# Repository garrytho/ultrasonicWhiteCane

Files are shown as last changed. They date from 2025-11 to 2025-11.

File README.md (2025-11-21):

# Ultrasonic Distance-Sensing White Cane
<table>
  <tr>
    <td align="center">
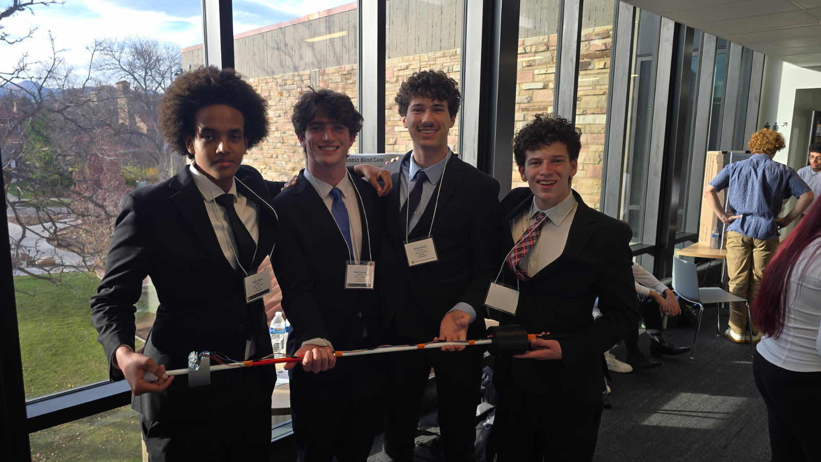
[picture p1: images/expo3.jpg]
      <br>
      <em>The fully assembled cane on expo day</em>
    </td>
    <td align="center">
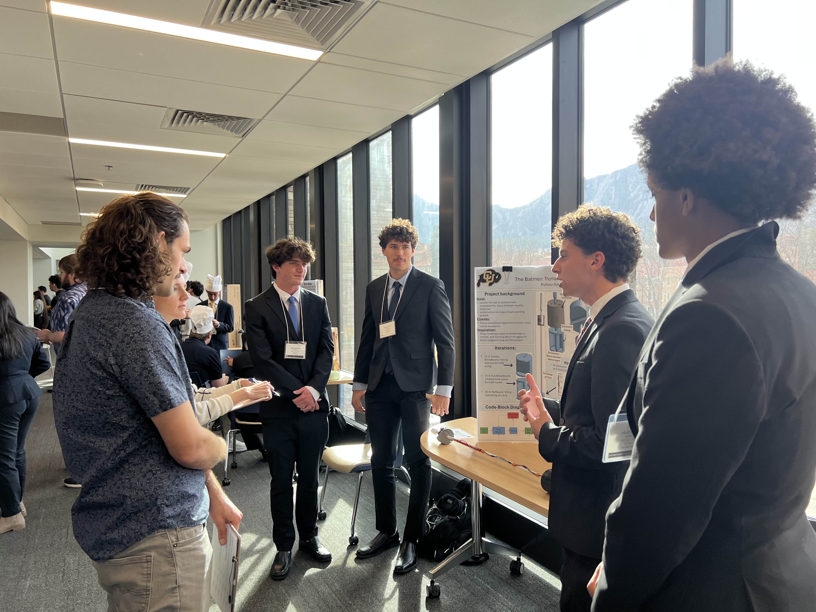
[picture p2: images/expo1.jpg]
      <br>
      <em>The team delivering the pitch</em>
    </td>
  </tr>
</table>

An Arduino-based cane for the visually impaired that uses a distance sensor and haptic feedback to give real time information about surroundings. 

## Update:
<table>
  <tr>
    <td align="center">
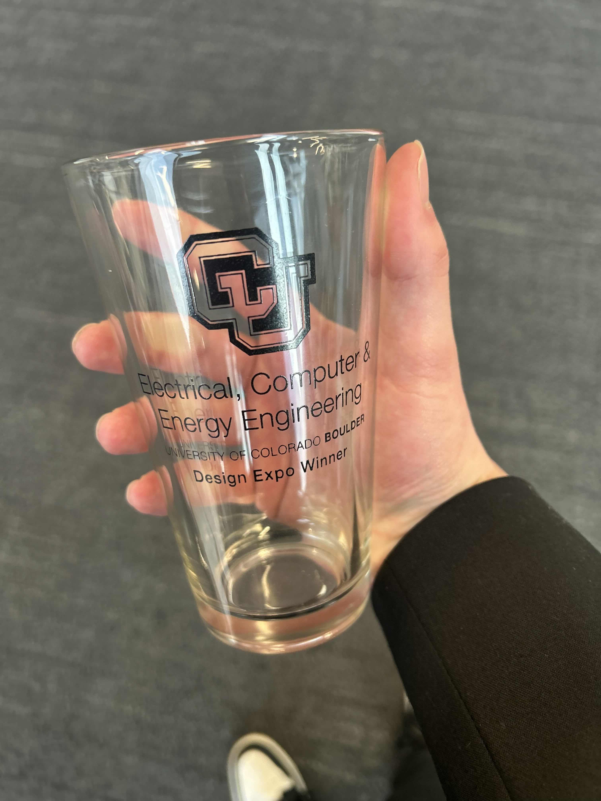
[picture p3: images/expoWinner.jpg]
      <br>
      <em>We are excited to announce that this project has won a freshman design award after judging at expo. 
</em>
  </tr>
</table>

## IMPORTANT:
This project is a work in progress. Iteration and modification may be necessary for reliable daily usage!

## Overview
Our project is a modified blind cane for the visually impaired that helps to reduce collisions while navigating. To accomplish this, we implemented an ultrasonic distance sensor along with a buzzer to alert the user when they are close to objects through vibration and sound. By using readily available components, 3D printed housing, and a pre-existing blind cane, we have created a widely accessible and affordable navigational aid. Our white cane is much cheaper to produce than commercially available alternatives, and is entirely open source for improvements and alterations. We hope that our resourceful design empowers more users with greater confidence and independence.

## Images and Demonstrations
<table>
  <tr>
    <td align="center">
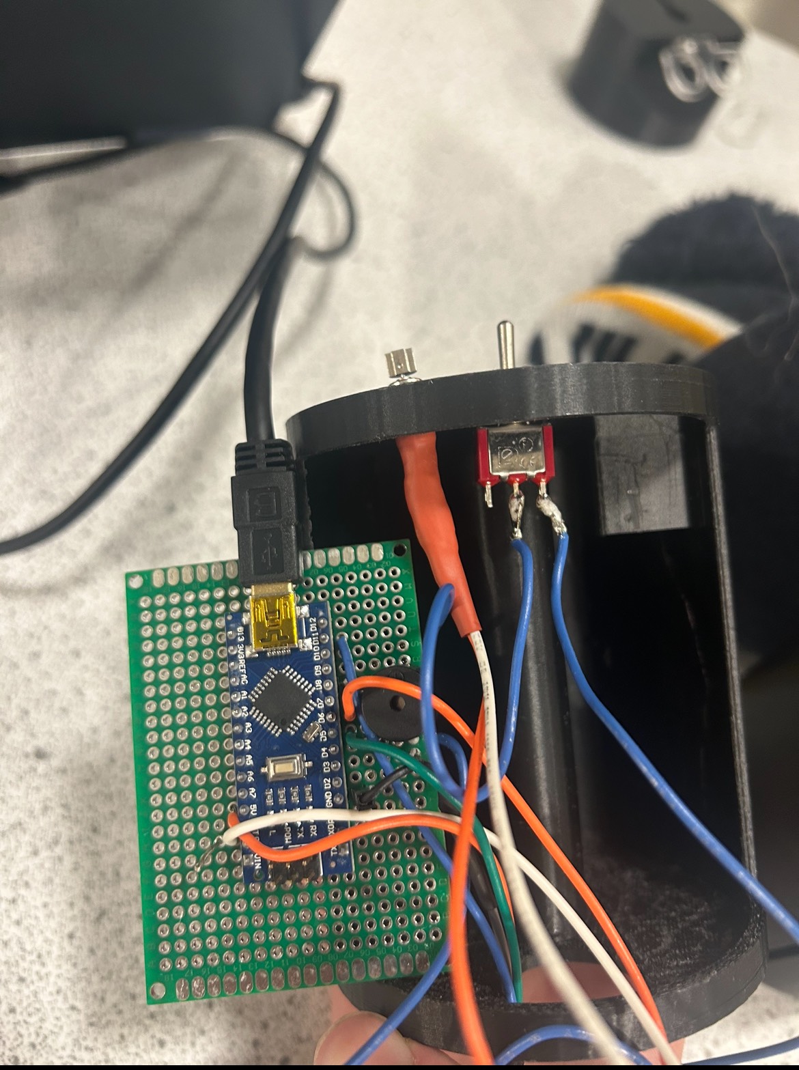
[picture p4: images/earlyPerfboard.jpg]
      <br>
      <em>Our first soldered perfboard being fitted into the case </em>
    </td>
    <td align="center">
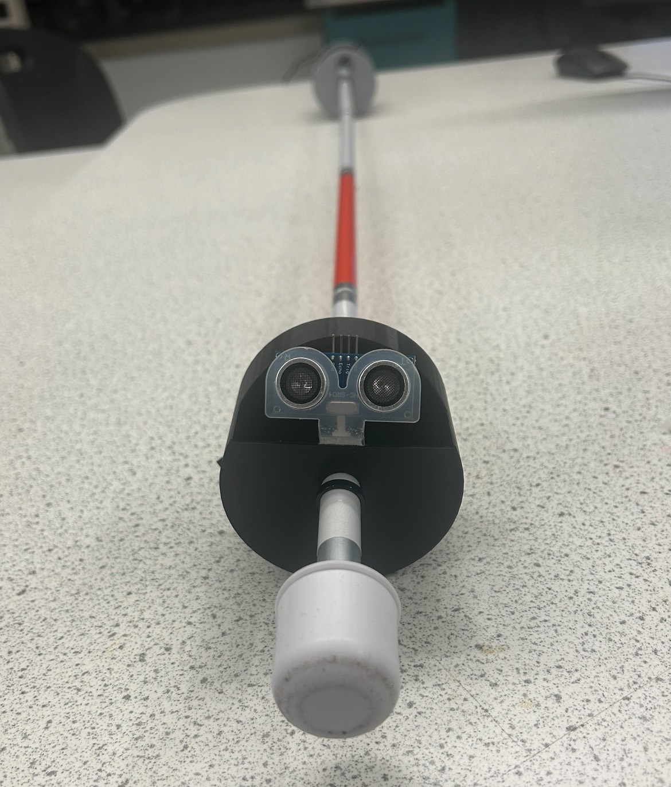
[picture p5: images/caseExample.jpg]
      <br>
      <em>The second iteration of the sensor mount </em>
    </td>
    <td align="center">
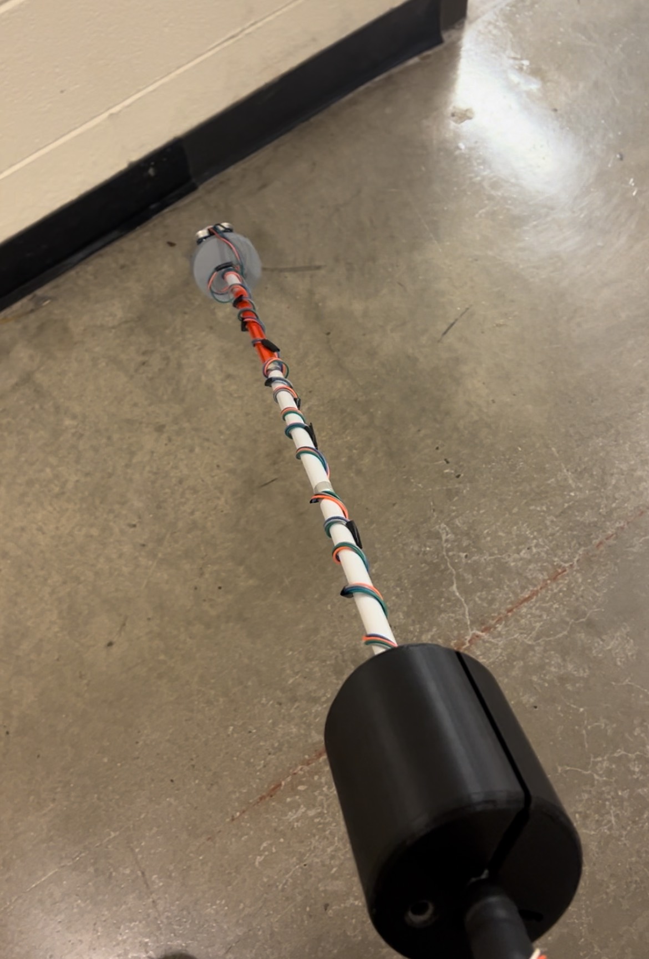
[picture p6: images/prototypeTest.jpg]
      <br>
      <em>A fully assembled initial prototype</em>
    </td>
  </tr>
</table>

### [Click here to watch the demo video](https://youtube.com/shorts/pAP-bUpbX8s?feature=share)

## Features
-Entirely open sourced
-Much cheaper to produce as compared to commercial alternatives
-Rechargable battery via USB-C for accessibility
-Weight distribution is optimal for daily navigation

## Cost of development vs. commercial alternatives

| Device | Price per Unit | Precision | Notes |
|--------|----------------|-----------|-------|
| [WeWalk Smart Cane 2](https://floridareading.com/products/wewalk-smart-cane-2-with-voice-assistant) | $1,050 | High | Extremely expensive, but has extensive features. |
| **This White Cane** | **~$51.69** | Mid | Highly affordable, and possible to build yourself. Open sourced for wider accessilibility and to encourage innovation in the assistive tech space. |

## Use Cases and Applications

# BILL OF MATERIALS

| # | Item               | Purpose           | Qty. | Cost/Unit Part | Cost |
|---|--------------------|------------------|------|----------------|------|
| 1 | HC-SR04            | Ultrasonic Sensor | 1    | $4             | $4   |
| 2 | Arduino Nano       | Microcontroller   | 1    | $5             | $5   |
| 3 | JYCL0610R2540      | Vibration Motor   | 3    | $2             | $6   |
| 4 | MakerFocus 3.7V 3000mAh Lipo | LiPo Batteries | 2 | $9 | $18 |
| 5 | MT3608             | Step Up           | 1    | $1             | $1   |
| 6 | TP4056             | Charge Protector  | 1    | $2             | $2   |
| 7 | Cane               | Cane              | 1    | $15            | $15  |
**Total:** $51

## Hardware Overview
<p align="center">
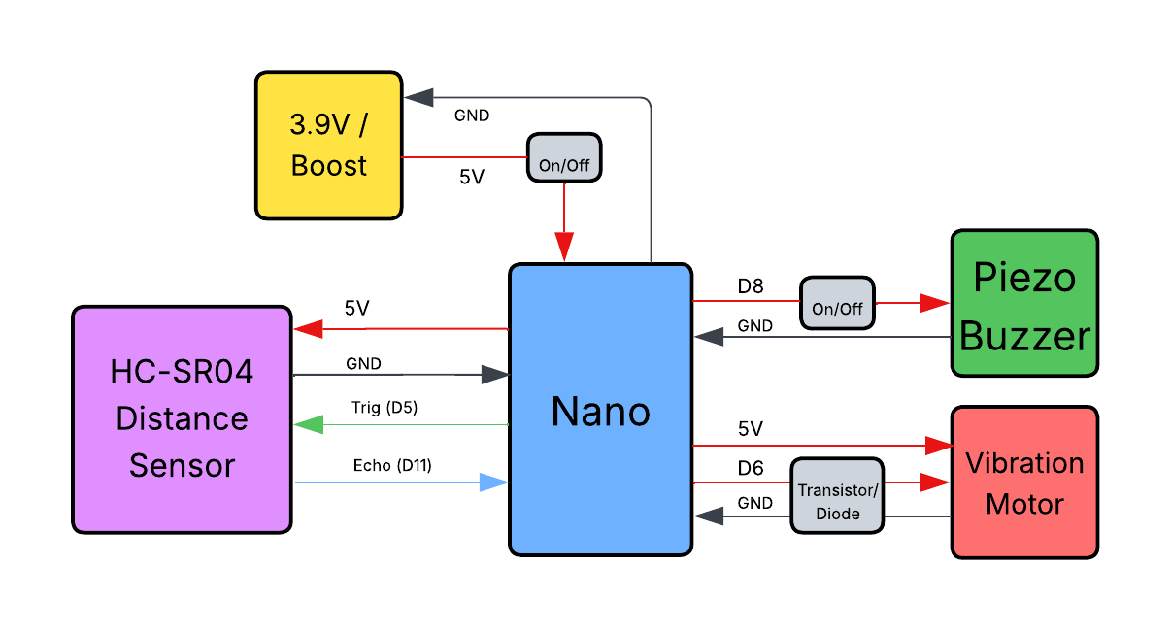
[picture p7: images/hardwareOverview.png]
  <br>
</p>

### Pin Assignments

**Power**:
- **+5v** - +5V from Boost Module
- **GND** - GND from Boost Module

**Distance Sensing**:
- **+5V** - VCC pin on the HC-SR04
- **GND** - GND pin on the HC-SR04
- **D5** - Trig pin on the HC-SR04
- **D11** - Echo pin on the HC-SR04

**Sound Cue**: 
- **D8** - VCC pin on the piezo buzzer
- **GND > Switch** - Toggles GND pin on the piezo buzzer (on/off)
  
**Haptic Cue**:
- **+5v** - VCC pin on vibration motor
- **D6** - Base pin on control transistor
- **GND > Transistor/Diode** - Emitter and collector lines for vibration motor control. 

### Setup Instructions
- Assemble the circuit as described above
- Connect the Arduino board to your computer via USB
- Open the provided .ino file in the Arduino IDE
- Select the appropriate port and board type (Nano)
- Upload the code to the Nano
- Disconnect from USB and power via LiPo

### Code Snippet
```cpp
//Take one distance reading (in cm)
long distance = pingDistance();

//Filter for valid readings
if (distance > 0 && distance < 120) {

  // Map distance to tone: closer = higher urgency
  int toneFreq = map(distance, 1, 120, 5000, 500);
  tone(8, toneFreq, 200);   // buzzer on pin 8

  // Vibration motor: full power at or below 60 cm
  if (distance <= 60) {
    analogWrite(vibPin, 255);   // ON
  } else {
    analogWrite(vibPin, 0);     // OFF
  }
}
```
For the full firmware, see [whiteCaneV6_Simplified_Clean.ino](whiteCaneV6_Simplified_Clean.ino)

### Hardware Limitations & Planned Improvements
| Issue                    | Description                                              | Planned Fix                                                                 |
|--------------------------|----------------------------------------------------------|------------------------------------------------------------------------------|
| Battery reliability      | 5V LIPO is vulnerable to weather interference.                  | Improve waterproofing and make the housing more robust|
| Sensor Accuracy      | The HC-SR04 alone can sometimes yield inconsistent results, especially with objects that scatter sound.                 | Integrate a second sensor (time of flight) and cross reference readings.|
| Housing       | Our current housing doesn't mechanically secure certain components in the circuitry box.                  | Add dedicated segments with mounting screws / threadded holes for securing components. |

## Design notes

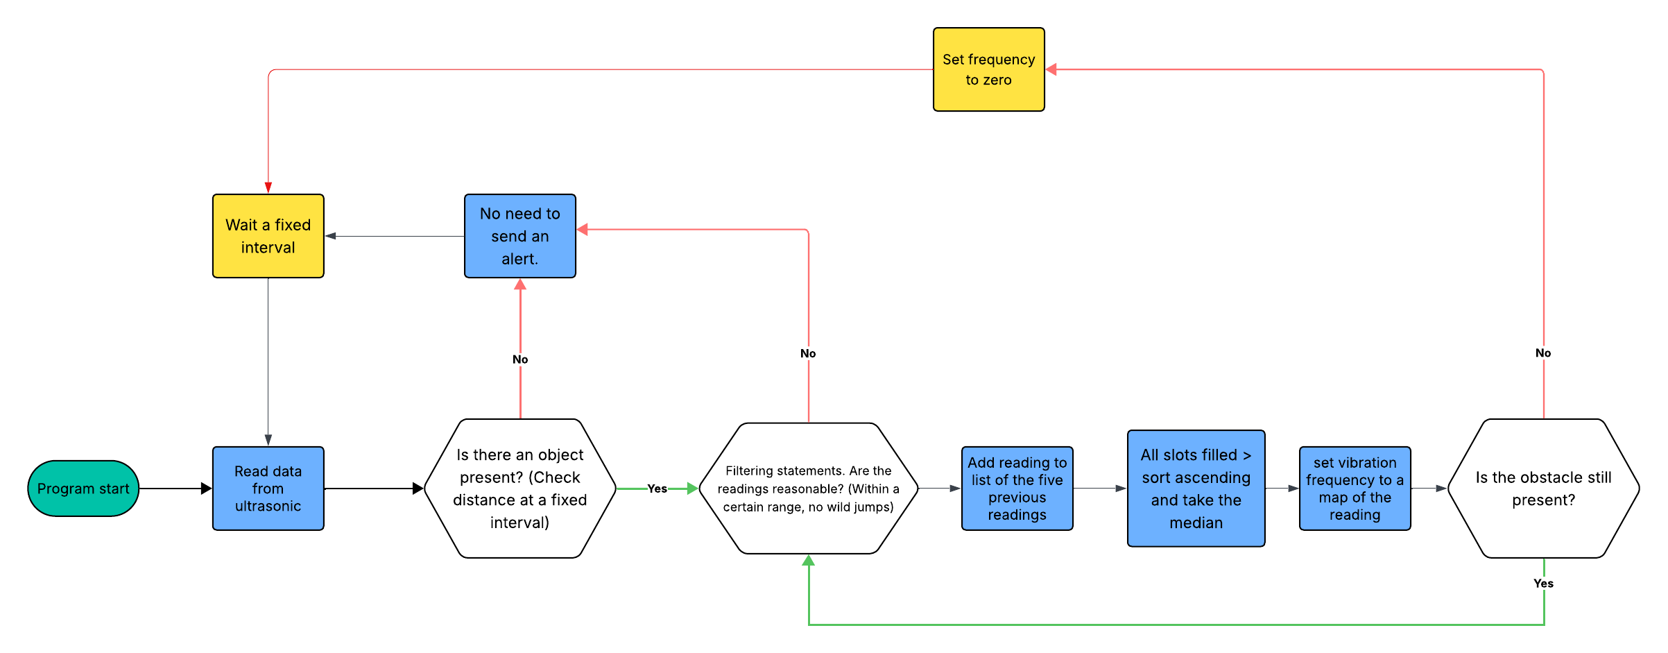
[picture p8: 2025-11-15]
images/codeOverview.png

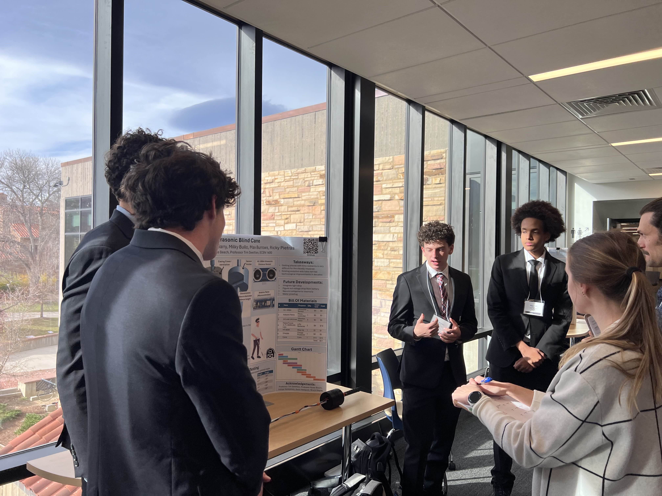
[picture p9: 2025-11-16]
images/expo2.jpg

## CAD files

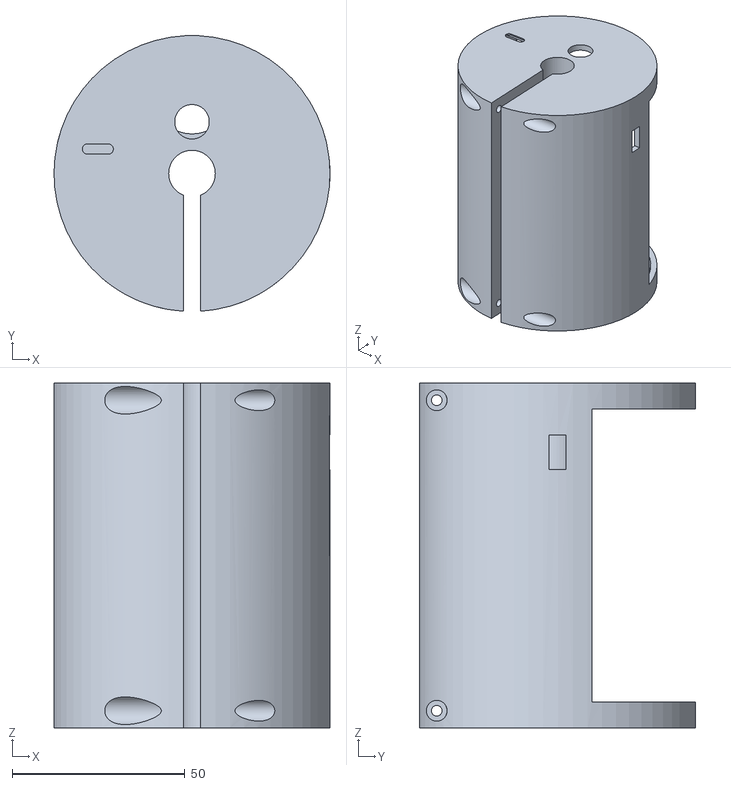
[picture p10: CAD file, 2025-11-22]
onShape/Main Housing V2.stl
80.0 x 79.9 x 100.0

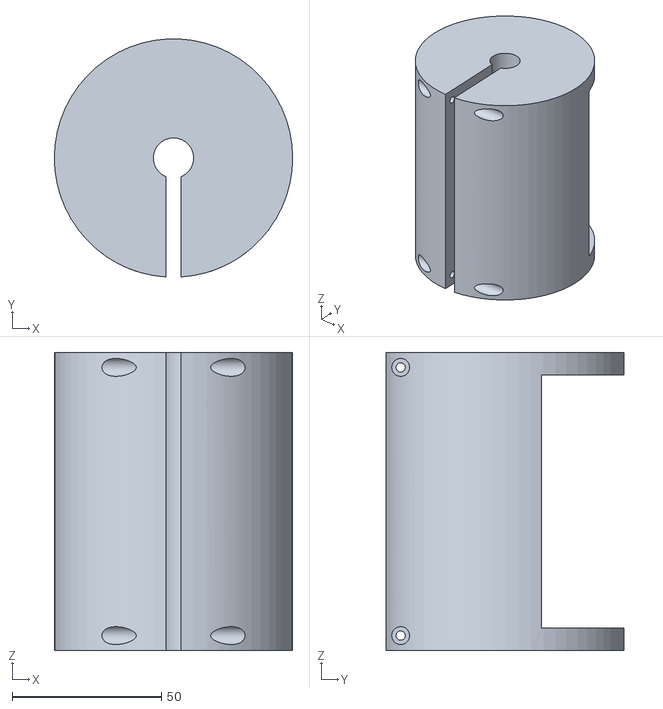
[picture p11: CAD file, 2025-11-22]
onShape/Main Housing V1.stl
80.0 x 79.9 x 100.0

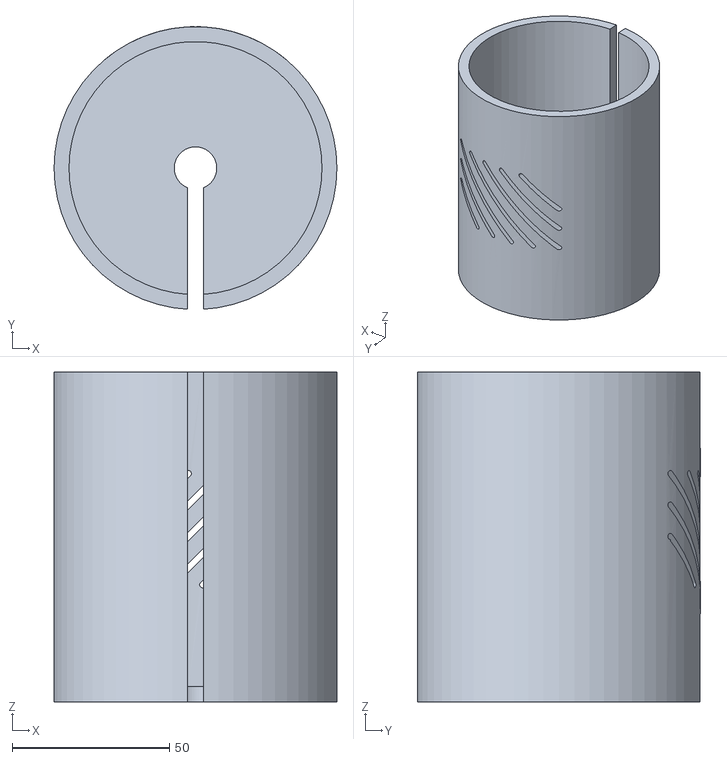
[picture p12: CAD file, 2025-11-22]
onShape/Casing V1.stl
90.0 x 89.9 x 105.0

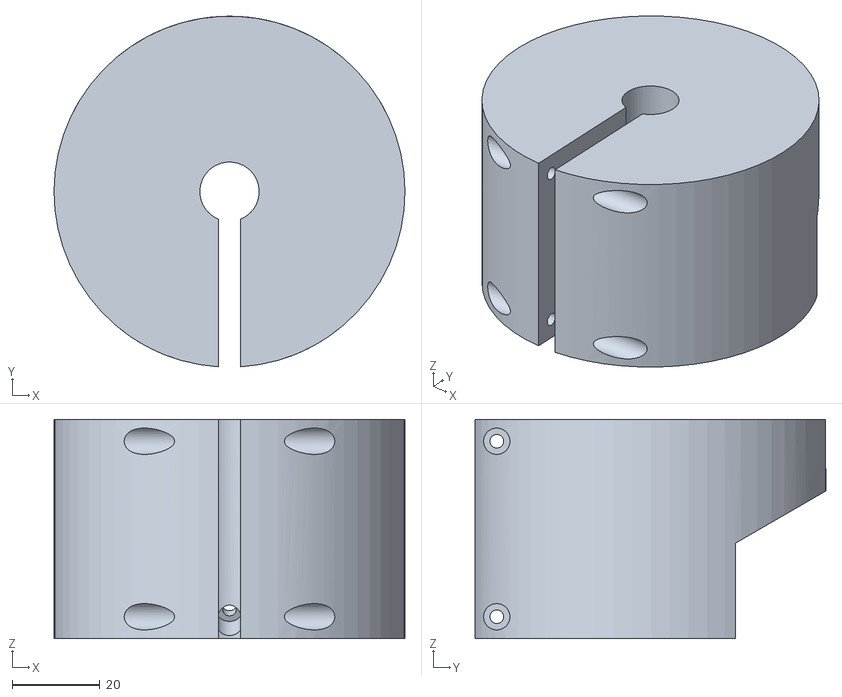
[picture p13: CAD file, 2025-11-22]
onShape/Sensor Holder V2.stl
80.0 x 79.9 x 50.0

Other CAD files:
onShape/Main Housing V3.stl
onShape/Sensor Holder V3.stl
onShape/Casing V3.stl

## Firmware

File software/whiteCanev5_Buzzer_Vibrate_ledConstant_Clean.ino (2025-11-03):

#include <Adafruit_NeoPixel.h>


//pin definitions for the distance sensor
int trig = 5;
int echo = 11;

//pin definition for the vibration motor
int vibPin = 6;

//pin definition for the led WS2812 strip
int ledPin = 2;

//variables for distance sensor filtering and tracking
long currentDistance;
int prevDistance;
int recentReadings[5];
int readingCount = -1;

//the amount of failed sensor values allowed before we turn off vibration
int missCount = 0;
int missThreshold = 5;

//variables for buzzer
int buzzPin = 8;
int toneFreq;

//variables for vibration motor
int prevVibrationIntensity = 0;
int vibrationIntensity;

//variables for led control
int ledBrightness = 255;
int ledCount = 26;
Adafruit_NeoPixel strip(ledCount, ledPin, NEO_GRB + NEO_KHZ800);



void setup() {
  // put your setup code here, to run once:
  Serial.begin(9600);

  //pinMode assignments
  pinMode(trig, OUTPUT);
  pinMode(echo, INPUT);
  pinMode(vibPin, OUTPUT);
  pinMode(ledPin, OUTPUT);

  //beginning the LED strip as a constant red LED.
  strip.begin();
  strip.show();
  strip.setBrightness(ledBrightness);
  strip.fill(strip.Color(255, 0, 0));
  strip.show();
}

//a bubble sort that sorts the global array currentReadings[] ascending
void sortAscending() {

  //specify the end component 
  const int n = sizeof(recentReadings) / sizeof(recentReadings[0]);

  //nested loops. standard bubble sort
  for (int i = 0; i < n - 1; ++i) {
    bool swapped = false;
    for (int j = 0; j < n - 1 - i; ++j) {
      if (recentReadings[j] > recentReadings[j + 1]) {
        int t = recentReadings[j];
        recentReadings[j] = recentReadings[j + 1];
        recentReadings[j + 1] = t;
        swapped = true;
      }
    }
    if (!swapped) break; //exit if already sorted
  }
}

long pingDistance() {
  // the ping sequence for our distance sensor, as per the datasheet
  digitalWrite(trig, LOW);
  delayMicroseconds(2);
  digitalWrite(trig, HIGH);
  delayMicroseconds(10);
  digitalWrite(trig, LOW);

  // this acts as a "stopwatch". tells you how long it took the ultrasonic wave to return.
  long duration = pulseIn(echo, HIGH);

  // converting that distance to a cm value, as per the datasheet
  long distance = duration / 58;

  // return the value we found
  return distance;
}

//converts the current distance in centimeters to one of three ranges.
int getDistanceRange(int cm){

  
  //the closest state. will be used to issue the harshest warning
  if(cm < 45){
    return 1;
  }

  //the second closest state. Moderate warning
  if(cm < 75){
    return 2;
  }

  //the farthest state
  if(cm < 100){
    return 3;
  }

  //a null state. Stop the buzzer
  else{
    return 0;
  }
}


void loop() {
  // put your main code here, to run repeatedly:

  //update the current distance
  currentDistance = pingDistance();
  delayMicroseconds(60); //as per datasheet

  // a general filter. This sensor will not read past 150cm. Also, account for a base state of 0
  if (currentDistance < 150 && currentDistance > 0) {

    // a more advanced filter. The sensor data must be within 5 cm of the previous one to count
    // Skip filter if prevDistance is 0 (startup or after bad readings)
    if (prevDistance == 0 || (currentDistance >= prevDistance - 5 && currentDistance <= prevDistance + 5)) {
      readingCount++;
      

      // using the array to log the value...
      if (readingCount < 5) {  // cap at four so no index out of bounds
        recentReadings[readingCount] = currentDistance;
      }

      // only output a tone if the reading count has filled up!
      if (readingCount > 4) {
        sortAscending();

        Serial.print("Median ");
        Serial.print(recentReadings[2]);
        Serial.print("  Intensity: ");
        Serial.print(vibrationIntensity);
        Serial.print("\n");

        //resetting the pointer for the next array iteration and update currentDistance to median
        readingCount = -1;
        currentDistance = recentReadings[2];
        // update the prev distance to the current distance
        prevDistance = currentDistance;


        //BUZZER CONTROLS:
        //map the distance (in cm) to a buzzer tone. Higher is be shriller
        toneFreq = map(int(currentDistance), 1, 300, 5000, 0);
        tone(buzzPin, toneFreq, 200);
      
        //VIBRATION CONTROLS:
        //decide the distance range and then vibrate the motor accordingly
        switch(getDistanceRange(currentDistance)){
          case 1: vibrationIntensity = 255; break;
          case 2: vibrationIntensity = 155; break;
          case 3: vibrationIntensity = 55;  break;
          case 0: vibrationIntensity = 0;   break;
        }

        //only analogWrite if the intensity has actually updated
          if(prevVibrationIntensity != vibrationIntensity){
            analogWrite(vibPin, vibrationIntensity);
          }

          prevVibrationIntensity = vibrationIntensity;
      }
    }
  } else {
    //bad reading, reset so next good reading is accepted
    prevDistance = 0;
    readingCount = -1;
    
    //turn off motor when no valid object detected
    vibrationIntensity = 0;
    analogWrite(vibPin, vibrationIntensity);
    prevVibrationIntensity = 0;
  }

  
}

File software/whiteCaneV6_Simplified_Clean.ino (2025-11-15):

//Pin definitions
int trig = 5;
int echo = 11;
int prevDistance;
int vibPin = 6;

//variabes for filtering window
int recentReadings[5];
int readingCount = -1;

//distance logging
long currentDistance;

//buzzer control
int toneFreq;

//valid readings, but fail the 5cm similarity gate
int proxMisses = 0;

//vibration control
int vibPin = 6;

void setup() {
  Serial.begin(9600);
  pinMode(trig, OUTPUT);
  pinMode(echo, INPUT);
  pinMode(vibPin, OUTPUT);
  analogWrite(vibPin, 0);
}

//bubble sort
void sortAscending() {
  const int n = sizeof(recentReadings) / sizeof(recentReadings[0]);
  for (int i = 0; i < n - 1; ++i) {
    bool swapped = false;
    for (int j = 0; j < n - 1 - i; ++j) {
      if (recentReadings[j] > recentReadings[j + 1]) {
        int t = recentReadings[j];
        recentReadings[j] = recentReadings[j + 1];
        recentReadings[j + 1] = t;
        swapped = true;
      }
    }
    if (!swapped) break;
  }
}

//returns the distance of an object in cm in accordance with the HC-SR04 datasheet
long pingDistance() {
  digitalWrite(trig, LOW);
  delayMicroseconds(2);
  digitalWrite(trig, HIGH);
  delayMicroseconds(10);
  digitalWrite(trig, LOW);

  long duration = pulseIn(echo, HIGH);
  long distance = duration / 58;
  return distance;
}

void loop() {
  //update the current distance
  currentDistance = pingDistance();
  delayMicroseconds(60); //as per datasheet

  //general filter: valid sensor range
  if (currentDistance < 120 && currentDistance > 0) {

    //setup for enforcing 5 cm proximity
    if (prevDistance == 0) {
      prevDistance = currentDistance;
      proxMisses = 0;                   
    }

    //enforce cm proximity gate after setup
    if (currentDistance >= prevDistance - 5 && currentDistance <= prevDistance + 5) {
      //this passes
      proxMisses = 0;
      readingCount++;

      //fill the array slot by slot
      if (readingCount < 5) {
        recentReadings[readingCount] = currentDistance;
      }

      //if the array full. sort and take the median. 
      if (readingCount > 4) {
        sortAscending();

        Serial.print("Median ");
        Serial.print(recentReadings[2]);
        Serial.print("\n");

        readingCount = -1;
        currentDistance = recentReadings[2];

        //map distance to tone
        toneFreq = map(int(currentDistance), 1, 300, 5000, 0);
        tone(8, toneFreq, 200);
      }

      //update prevDistance ONLY for accepted samples
      prevDistance = currentDistance;

    } else {
      //in-range but failed proximity gate
      proxMisses++;          

      //simple escape—after 3 proximity misses to reset the prevDistance. Stops the thread from getting locked. 
      if (proxMisses >= 3) {
        prevDistance = 0;               // next valid in-range sample will seed
        readingCount = -1;              // clear partial window
        proxMisses = 0;
      }

    }
  } else {
  //invalid: do nothing here
  }



    // ---------------- VIBRATION CONTROL ----------------
  //FULL POWER if at or below 60 cm
  if (currentDistance <= 60 && currentDistance > 0) {
    analogWrite(vibPin, 255);     //motor on
  } else {
    analogWrite(vibPin, 0);       //motor off
  }
  // ---------------------------------------------------

}

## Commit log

2025-10-17 Added Led BringUp code
2025-10-17 Added a V3 of the code that scales LED brightness with distance. Needs refinement for further use
2025-11-03 Updated pin definitions for perfboard soldering.
2025-11-15 Added flowchart diagrams for code and hardware
2025-11-22 Added files for CAD sketches and onshape links
    [Casing V1.stl, Casing V2.stl, Casing V3.stl, Main Housing V1.stl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]
